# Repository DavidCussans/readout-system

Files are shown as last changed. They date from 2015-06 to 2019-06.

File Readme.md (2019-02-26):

SoLid readout system
====================

_Development of the readout system for the full scale SoLid experiment._

The repository is split into the separate development parts:

* sensors - The light sensors and the PCBs
* analog board - to provide bias voltage, amplify and shape the analog signals form the sensors
* digital board - to digitise the analog signals, analyse the signals in an FPGA to make trigger decisions and transmit them to a PC
* software - to collect data transmitted from the FPGA, further reduce the data and write it to disk. The interface for operators to control the system
* cabling - to connect the senors to the analog board, the analog board to the digital board, power supplies to each board, etc.
* docs - system level documents such as requirements, reports, etc.
* utility_box   design info and documentation about the utility box

Permissions
-----------

The `Readout developers` group have write access, other members of the collaboration have read access.
If you need access contact Dan Saunders.

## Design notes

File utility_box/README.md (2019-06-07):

Tubing Rn dector

thermo tube  4mm inside , 6 mm outside.   To fit it on the rn detector the tube was warmed up.

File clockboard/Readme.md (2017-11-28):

Manufacturing Data for ADC+FPGA Readout Board
=============================================

_Data for PCB fabrication, list of components ( BoM ) , component assembly information._

N.B. This is a copy of information at https://svn2.phy.bris.ac.uk/svn/uob-hep-pc051a

Contains information for :

1) main board
* pc054a_toplevel-manufacturing-artwork-2017-04-27.zip ( Gerber artwork, ODB++ information )
* pc054a_toplevel.pdf ( Circuit schematic )
* pc054a_toplevel_27_assembly.pdf ( Assembly drawings )
* pc054a_toplevel_27.brd ( PCB database file in Cadence Allegro format )
2) FMC ( board that plugs onto FPGA board and couples to main board via VHDCI cable )
* pc054a_fmc-manufacturing-artwork-2017-02-07.zip ( Gerber artwork, ODB++ information )
* pc054a_fmc.pdf ( Circuit schematic )
* pc054a_toplevel_27_assembly.pdf  ( Assembly drawings )
* pc054a_fmc_08.brd ( PCB database file in Cadence Allegro format )

Contains information on how to modify power supply circuit for correct operation:

* pc054a_changes_to_psu.pdf

Contains bitstreams ( with different IP addresses ):

* bitstreams/

Contains prom files ( 4x SPI , s25fl512s-spi-x1_x2_x4 )

* prom_files

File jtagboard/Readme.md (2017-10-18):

Documentation about JTAG board.

Design files in Eagle.

Cable needed to control multiplexer. See https://docs.google.com/spreadsheets/d/1sPC1HHSBhcLIxRam0Nl7j7j9OBzJNn8TZ3wjZsIO86E/edit?usp=sharing

Script to set up Minnowboard GPIO: setup_gpio.sh

Script to select which HDMI interface is used: test_jtag_mltxer.py

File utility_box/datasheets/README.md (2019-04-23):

data sheets for the components used in the utility box. 

for technical info about the sensors and Raspberry Pi see in this repository :
constructiondocs\housing\EnvironmentANDinterlock

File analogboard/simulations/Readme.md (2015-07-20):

#Simulations of the amplifier board

Started by David Cussans and handed over to Wim Beaumont.

Simulations use [LTSpice](http://www.linear.com/designtools/software/) from [Linear Technolgies](http://www.linear.com/)

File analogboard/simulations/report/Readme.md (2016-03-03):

signaldccoupling  : proposal for DC signal coupling between analogue output and ADC

concidencecounts_1.odc  , spread sheet with results from peak finding with two MPPC's . 

related links :

 * presentation 26 jan http://indico.iihe.ac.be/indico/materialDisplay.py?contribId=0&materialId=slides&confId=945 
 * presentation http://indico.iihe.ac.be/indico/materialDisplay.py?contribId=3&materialId=slides&confId=928 
 
oscilloscope_short_2ch.m  : mathlab script to read the oscilloscope and find the peaks and coincidence 

zerrosuppress.m  : mathlab code to read a stored data file and find the nr of samples above thershold. 

# Report on Simulations

To produce write-up:

pdflatex solid_readout_considerations.tex

bibtex solid_readout_considerations.aux

pdflatex solid_readout_considerations.tex

pdflatex solid_readout_considerations.tex

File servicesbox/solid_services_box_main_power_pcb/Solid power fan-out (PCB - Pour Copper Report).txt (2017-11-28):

Pour Copper Report
------------------

Report File:        H:\Projects\SoLid\DCDC Test circuit\Solid Power Fanout\Solid power fan-out (PCB - Pour Copper Report).txt
Report Written:     Wednesday, January 18, 2017
Project Path:       H:\Projects\SoLid\DCDC Test circuit\Solid Power Fanout\Solid power fanout.prj
Design Path:        H:\Projects\SoLid\DCDC Test circuit\Solid Power Fanout\Solid power fan-out.pcb
Design Title:       
Created:            20/09/2016 07:58:07
Last Saved:         18/01/2017 12:43:25
Editing Time:       20600 min
Units:              mm (precision 1)

End Of Report.

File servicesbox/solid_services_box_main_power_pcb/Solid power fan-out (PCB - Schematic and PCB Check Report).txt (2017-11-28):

Schematic and PCB Check Report
------------------------------

Report File:        H:\Projects\SoLid\DCDC Test circuit\Solid Power Fanout\Solid power fan-out (PCB - Schematic and PCB Check Report).txt
Report Written:     Thursday, November 24, 2016
Project Path:       H:\Projects\SoLid\DCDC Test circuit\Solid Power Fanout\Solid power fanout.prj
Design Path:        H:\Projects\SoLid\DCDC Test circuit\Solid Power Fanout\Solid power fan-out.pcb
Design Title:       
Created:            20/09/2016 07:58:07
Last Saved:         31/10/2016 15:54:12
Editing Time:       18976 min
Units:              mm (precision 1)

Checking integrity of Schematic "H:\Projects\SoLid\DCDC Test circuit\Solid Power Fanout\Solid power fan-out.sch" with PCB "H:\Projects\SoLid\DCDC Test circuit\Solid Power Fanout\Solid power fan-out.pcb"
==========================================================================================================================================================================================================

The designs are the same.

End Of Report.

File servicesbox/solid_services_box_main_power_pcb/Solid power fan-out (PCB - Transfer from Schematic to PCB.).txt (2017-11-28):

Transfer from Schematic to PCB.
-------------------------------

Report File:        H:\Projects\SoLid\DCDC Test circuit\Solid power fan-out (PCB - Transfer from Schematic to PCB.).txt
Report Written:     Tuesday, September 20, 2016
Design Path:        H:\Projects\SoLid\DCDC Test circuit\Solid power fan-out.pcb
Design Title:       
Created:            20/09/2016 08:58:07
Last Saved:         20/09/2016 08:58:22
Editing Time:       0 min
Units:              mm (precision 1)

Net class "Power" was not defined, but has been created. Please check the values in the PCB design.

End Of Report.

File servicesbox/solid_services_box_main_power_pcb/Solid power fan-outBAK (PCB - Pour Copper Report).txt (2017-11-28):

Pour Copper Report
------------------

Report File:        H:\Projects\SoLid\DCDC Test circuit\Solid Power Fanout\Solid power fan-outBAK (PCB - Pour Copper Report).txt
Report Written:     Wednesday, October 26, 2016
Project Path:       H:\Projects\SoLid\DCDC Test circuit\Solid Power Fanout\Solid power fanout.prj
Design Path:        H:\Projects\SoLid\DCDC Test circuit\Solid Power Fanout\Solid power fan-outBAK.pcb
Design Title:       
Created:            20/09/2016 08:58:07
Last Saved:         26/10/2016 16:44:35
Editing Time:       12021 min
Units:              mm (precision 1)

End Of Report.

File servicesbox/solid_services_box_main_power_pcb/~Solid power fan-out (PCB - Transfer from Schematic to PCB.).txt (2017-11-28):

Transfer from Schematic to PCB.
-------------------------------

Report File:        H:\Projects\SoLid\DCDC Test circuit\~Solid power fan-out (PCB - Transfer from Schematic to PCB.).txt
Report Written:     Tuesday, September 13, 2016
Design Path:        H:\Projects\SoLid\DCDC Test circuit\~Solid power fan-out.pcb
Design Title:       
Created:            13/09/2016 16:46:20
Last Saved:         13/09/2016 16:46:33
Editing Time:       0 min
Units:              thou (precision 0)

Net class "Power" was not defined, but has been created. Please check the values in the PCB design.

End Of Report.

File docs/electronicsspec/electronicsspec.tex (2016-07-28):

\documentclass[a4paper]{article}

\RequirePackage{graphicx}
\usepackage{authblk}
\usepackage{cleveref}
\crefname{figure}{figure}{figures}
\usepackage{caption}
\usepackage[dvipsnames]{xcolor}
%\usepackage{subcaption}
\usepackage[UKenglish]{babel}
\usepackage{alltt}
\usepackage{afterpage}
\usepackage[text={16cm,25cm},centering]{geometry}
\usepackage{enumitem}
\setenumerate[1]{label=Req. \thesubsection.\arabic*.}
\setenumerate[2]{label=\arabic*.}

%\geometry{
%  a4paper,%
%  top=3cm,%
%  textwidth=16cm,% 
%  textheight=23.2cm,%
%  marginparsep=7pt,% 
%  marginparwidth=2.5cm%
%}

\renewcommand*{\familydefault}{\sfdefault}

\title{Specification for the SoLid read-out electronics}
\author[]{SoLid read-out team}
\newcommand{\version}{Version 1.0}
\date{\today\\\version}

\usepackage{fancyhdr}
\pagestyle{fancy}
\lhead{SoLid read-out electronics specification}
\rhead{\version, \today}

\newcommand{\must}[1]{\textcolor{red}{#1}}
\newcommand{\should}[1]{\textcolor{orange}{#1}}
\def\I2C{I$^2$C}

\begin{document}

\maketitle

\tableofcontents

\section{Introduction}

The SoLid read-out system includes the primary optical sensors (SiPMs), the electronics to control and collect data from them, and the firmware and software used to collect and store this data.
In addition to the SiPM data other data is collected about the temperature and humidity of the detector.

This specification covers the requirements for the PCBs that form the electronic parts of the read-out system:
\begin{itemize}
    \item SiPM boards, which each house a single SiPM sensor
    \item In-detector sensor boards, which house sensors to be deployed inside the detector frames and an in-detector sensor bus interface board, mounted on the frame.
    \item Analog boards, which provide bias control to the sensors and amplify the signals from them.
    \item Digital boards, which digitise the sensor data and feed it into the front-end FPGAs.
    \item Clock distribution boards, which fan-out a global clock to all digital boards.
    \item Power distribution boards, which fan-out power to the analog and digital boards.
    \item FPGA programming boards, which fan out JTAG to program the FPGAs.
\end{itemize}

\subsection{Major versions}

\begin{itemize}
    \item Version 0.0 of this spec is the first version. Minor versions (0.x) have been produced as the system design has evolved.
    \item Version 1.0 (XX Jun 16) of this spec should contain sufficient information to allow the design of the sensor, analog and digital read-out boards. Minor (1.x) versions may be made with the agreement of the team if changes must be made to the specification of analog and digital boards during the design and review phase.
    \item Later major versions will add details to the specification of the other electronics boards (in-detector sensor interface board, in-detector sensor boards, clock distribution board, power distribution board, FPGA programming board).
\end{itemize}

\section{PCB specifications}

The specifications for the various PCBs that will be designed are given in the following subsections.

\subsection{SiPM board}

{\bf Designer: Nick Ryder}

The SiPM boards each house a single SiPM and a connect to two twisted pairs of the SiPM ribbon cable.
One pair provides the bias voltage for the SiPM, the other acts as a ground/voltage reference.

\begin{figure}[h]
    \begin{center}
        
        \caption{Size of the SiPM board.}
        \label{fig:sipmboardsize}
    \end{center}
\end{figure}

\begin{table}[h]
    \begin{center}
        \caption{Pin mapping for the 4-way IDC socket on the SiPM board.}
        \label{tab:IDC4waySiPM}
        \begin{tabular}{cc}
            \hline
            \hline
            Pin & Function \\
            \hline
            1 & GND \\
            2 & GND \\
            3 & SiPM HV \\
            4 & SiPM LV \\
            \hline
            \hline
        \end{tabular}
    \end{center}
\end{table}

\begin{enumerate}
    \item \must{The SiPM board must fit within the existing 3D printed socket design, with dimensions as shown in \cref{fig:sipmboardsize}.}
    \item \must{The SiPM board must house a single S12752-050P SiPM.}
    \item \must{The SiPM board must connect to the SiPM ribbon cable using a 4-way 1.27 mm pitch IDC socket TE 7-188275-4 (Farnell 3784710).}
    \item \must{The 4-way IDE socket must be on the opposite side of the PCB to the SiPM.}
    \item \must{The socket pin connections must be as detailed in \cref{tab:IDC4waySiPM}, where pin 1 is closest to the polarisation pin of the connector. The matching connector on the ribbon cable will be TE 7-215083-4, (Farnell 149032).}
    \item \must{The cable used to connect to the SiPMs must be 1.27 mm pitch twist and flat ribbon cable, with coloured wires (such as 3M XXXX, Farnell XXXX).}
    \item \must{The PCB must be able to identify which specific SiPM sensor is soldered to it.}
    \item \should{The SiPM boards should be designed to ease the production of 3000 units.}
    \item \should{The PCB silkscreen should indicate which order the ribbon cable wires (either coloured or brown) correspond to the IDC socket.}
\end{enumerate}

\clearpage
\newpage
\subsection{In-detector sensor bus}

{\bf Designer: Wim Beaumont (and others?)}

An \I2C bus will be provided on a pair ribbon cables within each detector frame, to allow deployment of in-detector sensors.
Temperature and humidity sensors are expected to be deployed within the detector and other sensors or functionalities may be useful.
The sensor bus ribbon cables will connect to a dedicated sensor bus PCB attached to the covering plate on the detector frame.
This will be deployed below the two analog PCBs.
The 10-way ribbon cable will be split into two in-detector sensor buses.
On bus will have the \I2C and also two GPIO lines, the other will only have \I2C.
The sensor board interface PCB will be connected by a ribbon cable to the digital read-out board's \I2C buses.

\begin{enumerate}
    \item \must{The sensor interface PCB must connect to the two sensor ribbon cables using a 10-way IDC connector, 3M 4610-600 (Farnell 1758627) connector.}
    \item \must{The sensor interface PCB must connect to one 4-way and one 6-way sensor ribbon cable, each with a separate \I2C bus, as shown in \cref{tab:i2cbus}.}
    \item \must{The sensor interface PCB must be able to enable or disable power to the \I2C buses.}
\end{enumerate}

\begin{table}[h]
    \begin{center}
        \caption{Pin mapping for the 10-way IDC socket on the sensor board.}
        \label{tab:i2cbus}
        \begin{tabular}{cc|cc}
            \hline
            \hline
            \multicolumn{2}{c}{Bus 0} & \multicolumn{2}{c}{Bus 1}\\
            Pin & Function & Pin & Function \\
            \hline
            1 & 3.3 V & 7 & 3.3 V \\
            2 & SCL0 & 8 & SCL1 \\
            3 & SDA0 & 9 & SDA1 \\
            4 & GND & 10 & GND \\
            5 & NC / GPIO0? & & \\
            6 & NC / GPIO0? & & \\
            \hline
            \hline
        \end{tabular}
    \end{center}
\end{table}

The sensor boards themselves will potentially have multiple designs to meet the various needs.

\begin{enumerate}
    \item \must{The sensor board must connect to the sensor ribbon cable using either a 6-way 1.27 mm pitch IDC socket (TE 7-188275-6, Farnell 1056234) or a 4-way 1.277 mm IDC socket (TE 7-188275-4, Farnell 3784710).}
    \item \must{The socket pin connections must be as detailed in \cref{tab:indetectorpins}, where pin 1 is closest to the polarisation pin of the connector.}
    \item \must{Each sensor board should allow the selection of \I2C addresses per sensor.}
    \item \should{The cable used for the \I2C bus should be flat ribbon cable, visibly different from the twist and flat cable used for the SiPMs.}
\end{enumerate}

\begin{table}[h]
    \begin{center}
        \caption{Pin mapping for the 4-way and 6-way IDC sockets on the in-detector sensor boards.}
        \label{tab:indetectorpins}
        \begin{tabular}{cc|cc}
            \hline
            \hline
            \multicolumn{2}{c}{6-way bus} & \multicolumn{2}{c}{4-way bus}\\
            Pin & Function & Pin & Function \\
            \hline
            1 & 3.3 V & 1 & 3.3 V \\
            2 & SCL0 & 2 & SCL1 \\
            3 & SDA0 & 3 & SDA1 \\
            4 & GND & 4 & GND \\
            5 & NC / GPIO0? & & \\
            6 & NC / GPIO0? & & \\
            \hline
            \hline
        \end{tabular}
    \end{center}
\end{table}

\clearpage
\newpage
\subsection{Analog board}

{\bf Designer: Wim Beaumont}

The analog boards provide a programmable bias voltage to each SiPM and also amplify the signals from each SiPM.
Two analog boards will be used per detector plane.
All analog boards are identical.

\begin{figure}[h]
    \begin{center}
        
        \caption{Size of the analog board and positions of connectors.}
        \label{fig:analogboardsize}
    \end{center}
\end{figure}

\begin{figure}[h]
    \begin{center}
        
        \caption{Size and positions of both the analog and digital boards.}
        \label{fig:analogdigitalboardsize}
    \end{center}
\end{figure}

%\begin{figure}[h]
%    \begin{center}
%        \includegraphics[width=0.8\textwidth]{imgs/analogboardsize}
%        \caption{Size of the analog board and positions of connectors.}
%        \label{fig:analogboardsize}
%    \end{center}
%\end{figure}

\begin{table}[h]
    \begin{center}
        \caption{Pin mapping for the lower 64-way DIN41612 socket housed on the analog board for connecting to the SiPM ribbon cable. The pin pattern is repeated 16 times. Note that pins A/B1 are towards the lower edge of the board.}
        \label{tab:lowerIDC64way}
        \begin{tabular}{cc|cc}
            \hline
            \hline
            Pin & Function & Pin & Function \\
            \hline
            A(1+2N) & SiPM$_N$ HV & A(2+2N) & GND \\
            B(1+2N) & SiPM$_N$ LV & B(2+2N) & GND \\
            \hline
            \hline
        \end{tabular}
    \end{center}
\end{table}

\begin{table}[h]
    \begin{center}
        \caption{Pin mapping for the upper 64-way DIN41612 socket housed on the analog board for connecting to the SiPM ribbon cable. The pin pattern is repeated 16 times. Note that pins A/B1 are towards the lower edge of the board.}
        \label{tab:upperIDC64way}
        \begin{tabular}{cc|cc}
            \hline
            \hline
            Pin & Function & Pin & Function \\
            \hline
            A(1+2N) & SiPM$_{N+16}$ HV & A(2+2N) & GND \\
            B(1+2N) & SiPM$_{N+16}$ LV & B(2+2N) & GND \\
            \hline
            \hline
        \end{tabular}
    \end{center}
\end{table}

\begin{table}[h]
    \begin{center}
        \caption{Pin mapping for the 3-way low-voltage power connector.}
        \label{tab:LVPower}
        \begin{tabular}{cc}
            \hline
            \hline
            Pin & Function \\
            \hline
            1 & +5 V \\
            2 & GND \\
            3 & -3.3 V \\
            \hline
            \hline
        \end{tabular}
    \end{center}
\end{table}

\begin{table}[h]
    \begin{center}
        \caption{Pin mapping for the 2-way high-voltage power connector.}
        \label{tab:HVPower}
        \begin{tabular}{cc}
            \hline
            \hline
            Pin & Function \\
            \hline
            1 & HV $\le 80 V$ \\
            2 & GND \\
            \hline
            \hline
        \end{tabular}
    \end{center}
\end{table}

%\begin{table}[h]
%    \begin{center}
%        \caption{Pin mapping for the 10-way IDC socket housed on the analog board for connecting to the in-detector I2C bus.}
%        \label{tab:IDC10way}
%        \begin{tabular}{cc|cc|cc|cc|cc}
%            \hline
%            \hline
%            Pin & Function & Pin & Function & Pin & Function & Pin & Function & Pin & Function \\
%            \hline
%            1 & GND & 3 & 3.3 V & 5 & NC & 7 & GND & 9 & 3.3 V \\
%            2 & SDA0 & 4 & SCL0 & 6 & NC & 8 & SDA1 & 10 & SDA1 \\
%            \hline
%            \hline
%        \end{tabular}
%    \end{center}
%\end{table}

\begin{table}[h]
    \begin{center}
        \caption{Pin mapping for the upper 96-way DIN socket connecting the analog to the digital board. Note that pins A/B/C1 are towards the lower edge of the board.}
        \label{tab:DIN96Upper}
        \begin{tabular}{cc|cc|cc}
            \hline
            \hline
            Pin & Function & Pin & Function & Pin & Function \\
            \hline
            A1 & GND & B1 & GND & C1 & GND \\
            A2 & A16+ & B2 & GND & C2 & A17+ \\
            A3 & A16- & B3 & GND & C3 & A17- \\
            A4 & GND & B4 & GND & C4 & GND \\
            A5 & A18+ & B5 & GND & C5 & A19+ \\
            A6 & A18- & B6 & GND & C6 & A19- \\
            A7 & GND & B7 & GND & C7 & GND \\
            A8 & A20+ & B8 & GND & C8 & A21+ \\
            A9 & A20- & B9 & GND & C9 & A21- \\
            A10 & GND & B10 & GND & C10 & GND \\
            A11 & A22+ & B11 & GND & C11 & A23+ \\
            A12 & A22- & B12 & GND & C12 & A23- \\
            A13 & GND & B13 & GND & C13 & GND \\
            A14 & A24+ & B14 & GND & C14 & A25+ \\
            A15 & A24- & B15 & GND & C15 & A25- \\
            A16 & GND & B16 & GND & C16 & GND \\
            A17 & A26+ & B17 & GND & C17 & A27+ \\
            A18 & A26- & B18 & GND & C18 & A27- \\
            A19 & GND & B19 & GND & C19 & GND \\
            A20 & A28+ & B20 & GND & C20 & A29+ \\
            A21 & A28- & B21 & GND & C21 & A29- \\
            A22 & GND & B22 & GND & C22 & GND \\
            A23 & A30+ & B23 & GND & C23 & A31+ \\
            A24 & A30- & B24 & GND & C24 & A31- \\
            A25 & GND & B25 & GND & C25 & GND \\
            A26 & GPIO2 & B26 & GND & C26 & GPIO3 \\
            A27 & +3.3 V & B27 & GND & C27 & +1.8 V \\
            A28 & GND & B28 & GND & C28 & GND \\
            A29 & SDA0 & B29 & GND & C29 & SCL0 \\
            A30 & GND & B30 & GND & C30 & GND \\
            A31 & GND & B31 & GND & C31 & GND \\
            A32 & +5 V & B32 & GND & C32 & +5 V \\
            \hline
            \hline
        \end{tabular}
    \end{center}
\end{table}

\begin{table}[h]
    \begin{center}
        \caption{Pin mapping for the lower 96-way DIN socket connecting the analog to the digital board. Note that pin A/B/C1 are towards the lower edge of the board.}
        \label{tab:DIN96Lower}
        \begin{tabular}{cc|cc|cc}
            \hline
            \hline
            Pin & Function & Pin & Function & Pin & Function \\
            \hline
            A1 & GND & B1 & GND & C1 & GND \\
            A2 & A0+ & B2 & GND & C2 & A1+ \\
            A3 & A0 & B3 & GND & C3 & A1- \\
            A4 & GND & B4 & GND & C4 & GND \\
            A5 & A2+ & B5 & GND & C5 & A3+ \\
            A6 & A2- & B6 & GND & C6 & A3- \\
            A7 & GND & B7 & GND & C7 & GND \\
            A8 & A4+ & B8 & GND & C8 & A5+ \\
            A9 & A4- & B9 & GND & C9 & A5- \\
            A10 & GND & B10 & GND & C10 & GND \\
            A11 & A6+ & B11 & GND & C11 & A7+ \\
            A12 & A6- & B12 & GND & C12 & A7- \\
            A13 & GND & B13 & GND & C13 & GND \\
            A14 & A8+ & B14 & GND & C14 & A9+ \\
            A15 & A8- & B15 & GND & C15 & A9- \\
            A16 & GND & B16 & GND & C16 & GND \\
            A17 & A10+ & B17 & GND & C17 & A11+ \\
            A18 & A10- & B18 & GND & C18 & A11- \\
            A19 & GND & B19 & GND & C19 & GND \\
            A20 & A12+ & B20 & GND & C20 & A13+ \\
            A21 & A12- & B21 & GND & C21 & A13- \\
            A22 & GND & B22 & GND & C22 & GND \\
            A23 & A14+ & B23 & GND & C23 & A15+ \\
            A24 & A14- & B24 & GND & C24 & A15- \\
            A25 & GND & B25 & GND & C25 & GND \\
            A26 & GPIO0 & B26 & GND & C26 & GPIO1 \\
            A27 & +3.3 V & B27 & GND & C27 & +1.8 V \\
            A28 & GND & B28 & GND & C28 & GND \\
            A29 & SDA1 & B29 & GND & C29 & SCL1 \\
            A30 & GND & B30 & GND & C30 & GND \\
            A31 & GND & B31 & GND & C31 & GND \\
            A32 & +5 V & B32 & GND & C32 & +5 V \\
            \hline
            \hline
        \end{tabular}
    \end{center}
\end{table}

\begin{enumerate}
    \item \must{The analog board height (as shown in \cref{fig:analogboardsize}) must be 220 mm.}
    \item \should{The analog board width should be 150 mm.}
    \item \must{The analog board must connect to two 16-SiPM ribbon cables via a 64-way 1.27mm pitch DIN41612 plug connector each (Farnell 1096830).}
    \item \must{The pin mapping for each IDC socket connectiong to the SiPM ribbon cables must be as described in \cref{tab:lowerIDC64way,tab:upperIDC64way}, with pin1 on the lower edge of the connector and row A {\bf on which side?}.}
    \item \must{The analog board must connect to the digital board using two 96-way DIN41612 socket connectors (Farnell 1096942).}
    \item \must{The pin mapping for the two connectors to the digital board must be as described in \cref{tab:DIN96Upper,tab:DIN96Lower}, with pins A/B/C1 on the lower edge of the connector and row A {\bf on which side?}}
    \item \must{The position of the two connectors to the digital board must be as shown in \cref{fig:analogboardsize}.}
    \item \must{The analog board must use input power connections of -3.1, GND, + 4.7 V (supplied by remote -3.3 V and +5 V power supplies), using a Molex 22-23-2031 connector (Farnell 1462950).}
    \item \must{The pin mapping for the low voltage connector must be as shown in \cref{tab:LVPower}, where pin 1 is defined as the left-most pin when the polarising shroud is upper-most.}
    \item \must{The analog board must regulate the input power to -2.8, GND, +4.4 V using linear regulators.}
    \item \must{The regulators must be controllable from the digital board to enable or disable powering the analog board components.}
    \item \must{The analog board must amplify the signal from each of 32 SiPMs using an AD8132 amplifier.}
    \item \should{The analog board should be compatible with replacing the DC connection to the digital board with an AC connection by replacing only passive components and not using the negative voltage power supply.}
    \item \must{The analog board must use high voltage input connections using a connector that is incompatible with the low voltage connector (perhaps JST VHR-2N (RS 820-1172).}
    \item \must{The pin mapping of the high voltage input must be as shown in \cref{fig:HVPower}, where pin 1 is defined as...}
    \item \must{A fuse must be used to protect the board from excessive current from the HV supply, to break at $I \le 100$ mA.}
    \item \should{The high- and low-voltage supply connectors should be clearly labelled on the PCB.}
    \item \must{The analog board must be able to produce a programmable high voltage bias supply on board, using ADL5317.}
    \item \must{The analog board must provide a per SiPM low voltage trim of up to 4 V using programmable DACs.}
    \item \must{The programmable DACs must be controllable by from the digital board via the \I2C buses on the two 96-way connectors.}
    \item \should{The channel numbering of the DACs should map simply to the channel numbering of the SiPMs.}
    \item \must{The analog board must provide an on-board temperature measurement and unique ID using an ATMEL AT30TSE752 chip with an \I2C address of 0b1001000 (i.e. all address pins connected to GND).} 
    \item \should{The temperature alert line from the temperature chip should be connected to one of the GPIO pins on the 96-way DIN connectors.}
\end{enumerate}

\clearpage
\newpage

\subsection{Digital board}

{\bf Designer: David Cussans}

The digital boards house an FPGA board which does front end processing and triggering.
They also digitise the amplified signals from the analog boards.
Each detector plane will use a single digital board, receiving data from two analog boards, as shown in \cref{fig:analogdigitalboardsize}.

%\begin{figure}[h]
%    \begin{center}
%        \includegraphics[width=0.8\textwidth]{imgs/digitalboardsize}
%        \caption{Size of the digital board and positions of connectors.}
%        \label{fig:digitalboardsize}
%    \end{center}
%\end{figure}

\begin{table}[h]
    \begin{center}
        \caption{LVDS pins available for ADC data on the Trenz 0712.}
        \label{tab:TrenzLVDS}
        \begin{tabular}{cccc}
            \hline
            \hline
            Connector & Bank & Pairs & \# Pairs \\
            \hline
            JM1 & 13 & 3, 5, 6, 9, 11 & 5 \\
            %JM1 & 16 & 16, 19, 17, 18, 9, 7, 11, 10, 5, 2, 6, 4, 1, 22, 24, 23, 15, 20, 21, 13, 14, 3, 12, 8 &  24 & 29 \\
            JM1 & 16 & 1-24 & 24 \\
            JM2 & 13 & 1, 2, 4, 10, 12-17 & 10 \\
            JM3 &  15 & 1-24 & 24 \\
            \hline
            \multicolumn{3}{c}{Total} & 63 \\
            \hline
            \hline
        \end{tabular}
    \end{center}
\end{table}

\begin{table}[h]
    \begin{center}
        \caption{Pin uses for Trenz 0712 bank 14 (3.3 V).}
        \label{tab:TrenzB14}
        \begin{tabular}{cc}
            \hline
            \hline
            Usage & \# pins \\
            \hline
            1 channel ADC data & 2 \\
            CPLD \I2C/SPI device select & 5 \\
            CPLD SPI (MOSI, MISO, CLK) or \I2C (SCL, SDAI, SDAO) & 3 \\
            %CPLD \I2C (SCL, SDAI, SDAO) & 3 \\
            Analog board GPIO & 8 \\
            LEDs & 4 \\
            IP address switches & 8 \\
            \hline
            Total & 30 / 30 \\
            \hline
            \hline
        \end{tabular}
    \end{center}
\end{table}

\begin{table}[h]
    \begin{center}
        \caption{Pin information for the HDMI connector used for the clock and synchronisation signals.}
        \label{tab:ClockSyncPins}
        \begin{tabular}{cc|cc|cc}
            \hline
            \hline
            Pin & Function & Pin & Function & Pin & Function \\
            \hline
            1 & SYNC+ & 2 & SYNC shield  & 3 & SYNC- \\
            4 & NC? & 5 & NC? & 6 & NC? \\
            7 & CLK+ & 8 & CLK shield & 9 & CLK- \\
            10 & NC? & 11 & NC? & 12 & NC? \\
            13 & Power Enable? & 14 & NC? & 15 & NC? \\
            16 & NC? & 17 & NC? & 18 & NC? \\
            19 & NC? & & & & \\
            \hline
            \hline
        \end{tabular}
    \end{center}
\end{table}

\begin{table}[h]
    \begin{center}
        \caption{Pin mapping for the connection between the digital board and \I2C interface board. {\bf To be defined...}}
        \label{tab:digitalToI2CInterface}
        \begin{tabular}{cc|cc}
            \hline
            \hline
            Pin & Function & Pin & Function \\
            \hline
            1 & ? & 6 & ? \\
            2 & ? & 7 & ? \\
            3 & ? & 8 & ? \\
            4 & ? & 9 & ? \\
            5 & ? & 10 & ? \\
            \hline
            \hline
        \end{tabular}
    \end{center}
\end{table}

\begin{enumerate}
    \item \should{The digital board height (as shown in \cref{fig:analogdigitalboardsize}) should be 466.2 mm.}
    \item \should{The digital board width should be 160 mm.}
    \item \must{The digital board must connect to the analog boards using two 96-way DIN41612 plug connectors (Farnell 1096905).}
    \item \must{The pin mapping for the connectors to the analog board must be as described in \cref{tab:DIN96Upper,tab:DIN96Lower}.}
    \item \must{The position of the two 96-way DIN41612 connectors must allow the analog boards' connectors to be be as shown in \cref{fig:analogboardsize}, with the spacing between the two analog boards as shown in \cref{fig:analogdigitalboardsize}.}
    \item \must{The digital board must allow a Trenz 0712 board to be plugged in.}
    \item \must{The pin usage/mapping for the Trenz board connections must be as shown in \cref{tab:TrenzLVDS,tab:TrenzB14}.}
    \item \must{The digital board must digitise 64 SiPM channels using 8 LTM9007 ADCs.}
    \item \must{The ADCs must be controlled via a 16-channel SPI-like bus, with two chip select lines per ADC chip.}
    \item \must{The digital board must have an HDMI connector to receive a clock and synchronisation signal, with the pin connection as shown in \cref{tab:ClockSyncPins}.}
    \item \must{The digital board must have an on board SiXXXX chip to clean the external clock signal and provide the clocks for the ADC chips and FPGA.}
    \item \must{The SiXXXX clock chip must be controlled by an \I2C bus on the digital board.}
    \item \must{The digital board must have an SFP+ cage for a Gbps Ethernet connection.}
    \item \must{The digital board must use input power connections of GND and 5 V.}
    \item \must{The digital board must convert the input power to 1.8 V and 3.3 V using on-board switching DC-DC converters.}
    \item \must{The DC-DC converters must be controllable from the FPGA, to enable/disable powering of the ADC.}
    \item \must{The powering of the FPGA should be controllable remotely via a control line on the HDMI clock/sync bus.}
    \item \must{The digital board should include a temperature sensor that can power down the FPGA if the board temperature exceeds a programmable alarm threshold.}
    \item \must{The digital board must have two eSATA sockets to allow Gbps serial communications between FPGAs from neighbouring planes.}
    \item \must{The digital board must have a 10-way IDC ribbon cable socket to connect to the in-detector sensor \I2C interface board.}
    \item \must{The connections to the \I2C interface board should be as defined in \cref{tab:digitalToI2CInterface}.}
\end{enumerate}

\clearpage
\newpage
\subsection{Clock distribution board}

{\bf Designer: David Cussans}

The clock distribution board provides the same clock to all digital boards.
In addition the board is able to provide a synchronous pulsed signal to all boards to ensure synchronisation across the detector.

\begin{enumerate}
    \item \must{The clock distribution board must provide a xxx MHz clock to all digital boards.}
    \item \must{The clock distribution board must provide a pulse signal synchronously to ten digital boards.}
    \item \must{It must be possible to enable or disable the synchronisation pulses from software.}
    \item \must{The clock and synchronisation signals must be provided via an HDMI connector.}
    \item \must{The HDMI connector pin mapping must be as shown in \cref{tab:ClockSyncPins}.}
    \item \must{The clock distribution system must have a hierarchical design. Each module of 10 detector planes should be served by a single clock distribution board, which in turn is served by a global 1:10 clock distribution board.}
    \item \should{The FPGA controlling the clock system should have a firmware tool chain compatible with the Artix-7 that will be used on the read-out board.}
\end{enumerate}

\clearpage
\newpage
\subsection{Power distribution board}

{\bf Designer: ?}

Power distribution boards should provide ten detector planes with the necessary high and low voltage power...

\clearpage
\newpage
\subsection{FPGA programming board}

{\bf Designer: Bristol electronics design group}

Each module of ten detector planes will have an FPGA programming board.
This will house a network accessible computer running the Xilinx programming software.
The board will fan out JTAG connections to each of the ten FPGAs in the detector module.

\clearpage
\newpage

\section{Review process}

The analog and digital schematics will be internally reviewed.
Following completion of the lay out for the two boards they will be reviewed by internal and external reviewers.
This review will have a larger scope, including the system level design of the read-out system.

\section{Time schedule}

This is the time schedule discussed at the collaboration meeting at Imperial in May 2016.
It is based around designing and reviewing the design before producing sufficient electronics to instrument 5 detector planes.
These will then be tested and validated before starting a larger production for 50 planes.

\begin{figure}[h]
    \begin{center}
        
        \caption{Estimated schedule, where task 10 corresponds to the electronics described in this specification.}
        \label{fig:gantt}
    \end{center}
\end{figure}

\end{document}

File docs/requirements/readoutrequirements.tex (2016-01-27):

\documentclass[a4paper]{article}

\RequirePackage{graphicx}
\usepackage{authblk}
%\usepackage{cleveref}
\usepackage{caption}
%\usepackage{subcaption}
\usepackage[UKenglish]{babel}
\usepackage{alltt}
\usepackage{afterpage}
\usepackage[text={16cm,25cm},centering]{geometry}

%\geometry{
%  a4paper,%
%  top=3cm,%
%  textwidth=16cm,% 
%  textheight=23.2cm,%
%  marginparsep=7pt,% 
%  marginparwidth=2.5cm%
%}

\renewcommand*{\familydefault}{\sfdefault}

\title{Requirements for the SoLid read-out system}
\author[]{SoLid collaboration}
\date{\today\\V0.2}

\begin{document}

\maketitle

\tableofcontents

\section{Introduction}

This document defines the requirements for the full scale SoLid experiment's read-out system (the scope of which is defined below).
The purpose of the requirements is to ensure that the read-out system that will be produced will perform the necessary functionality for the SoLid experiment to be successful.
Two forms of requirements are defined.
Mandatory requirements use the term `must', whilst the term `should' is used for requirements which are desirably but not mandatory.
The requirements constrain the the overall design of the system, but should not constrain specific implementations.
For example, it is a requirement that there be a neutron trigger but not a requirement that a specific algorithm be used for the trigger.
During the design phase of the read-out system development the requirements may be updated, but once the initial version is agreed by the collaboration it is hoped that major changes will not be required.

\subsection{Scope of the read-out system}

The read out system includes the photo sensors (likely Silicon Photomultipliers or SiPMs), all electronics used to bias the sensors and store data collected from them, the software used to control the electronics,  the computing systems and software used to store and transmit the data out of SCK and the user interfaces to that software. 
The read out system does not include the scintillators, wavelength shifting fibres, mechanical frames, shielding, etc. that forms the physical detector. 
The read out system also does not include any software or computing systems used for data analysis or storage once the data is transmitted out of SCK.

\section{Requirements}

The requirements are split into a number of categories.
The physics requirements are those that are constrained by the need to perform the physics analyses (an oscillation search and spectrum measurement) planned for the experiment.
The infrastructure requirements are constrained by the infrastructure availability at BR2.
The operational requirements define how an operator should be able to control the experiment.
The budget requirements cover the time and cost constraints on the system.

\subsection{Physics requirements}

\renewcommand*{\theenumi}{\thesubsection.\arabic{enumi}}
\renewcommand*{\theenumii}{\thesubsection.\arabic{enumii}}
\begin{enumerate}
\item Neutron trigger - The system must be able to trigger on neutron signals coming from one vertical and one horizontal fibre in the same plane. 
    The neutron trigger should be x \% efficient for neutrons captured in the $^6$LiF:ZnS(Ag) layer. 
    For each neutron trigger the system must be able to store at least 0.5 ms of data from relevant channels around the neutron ID. 
    These requirements will ensure that the IBD trigger efficiency is independent of the positron energy and that the trigger rate does not strongly depend upon background signal rates.
\item Threshold trigger - The system must be able to trigger when a signal above a defined threshold is detected from one or more fibres in coincidence.
    This will allow measurement of efficiency of the neutron trigger and calibration running without neutron signals.
\item Random trigger -  The system must be able to be randomly triggered. 
    This will allow measurements of low amplitude signals.
\item Cosmic muon trigger - The system should be able to trigger on a the signal from a cosmic ray muon crossing many scintillator cubes. 
    For each cosmic ray trigger the system must be able to store relevant data in a time window around the trigger. 
    This will allow studies of cosmic ray related background events.
\item Energy range - Each channel must have a large enough range that a cosmic muon crossing a horizontal fibre does not normally saturate the range. 
    This will allow the use of cosmic rays for energy calibration. 
\item Channel resolution - Each channel must have a high enough resolution that the single photon amplitude can be measured. 
    This will allow the channel uniformity and stability to be measured and ensure that the read out system does not limit the energy resolution of the detector.
\item Noise - The read out system will introduce analog and digital noise to the signals from the sensors. 
    The combined noise from the read out system must be less than a single photon detection and should be less than 0.1 photons.
\item Channel uniformity - The readout system must be capable of supplying all channels with an over voltage that is uniform within x \%. 
    This will limit systematic variations in the measurement of IBD candidates at different locations within the detector.
\item Channel stability - The readout system must be cable of maintaining an over voltage that is stable within x \% over the five years of operation. 
    This will limit systematic variations in the measurement of IBD candidates in reactor on/off cycles.
\item Dead time - The system should not have any dead time. The system must store information to allow the calculation of the amount of dead time, the time at which it occurred and the channels effected.
\item Number of channels - The system must be capable of scaling up to take data from at least 6000 channels. 
    This will allow the detector volume to be increased using the same read out design should additional modules be funded.  
\item Experiment duration - The system should be capable of running for five years. 
    This will allow a sensitive search for short baseline oscillations.
\item Data required - The system must store the following data: 
    \begin{itemize}
    \item The time, position and waveform for signals identified as neutrons
    \item Enough data to extract the time, position and number of photons of any signals identified as coming from the PVT within a time window of -x and +y around the neutron trigger
    \item The over voltage supplied to all channels at all times during the experiment.
    \item The temperature and any other local conditions measured during the experiment.
    \item The start/end times and the trigger conditions for any data run.   
    \end{itemize}
    This will provide enough information to perform an oscillation analysis.
\end{enumerate}

\subsection{Infrastructure requirements}

\begin{enumerate}
\item A single optical Ethernet connection can be used to transfer data from the detector to the computing room at BR2.
\item x is provided to power the read out system.
\item The total bandwidth of data transmitted out of SCK should be limited to x GB/day.
\item x, y, z are not allowed within the containment building.
\end{enumerate}

\subsection{Operational requirements}

\begin{enumerate}
\item Operators must be able to set a uniform over voltage on a set of channels. 
\item Operators must be able to set a uniform bias voltage on a set of channels.
\item Updating the bias voltage of all channels should take less than 30 s.
\item Operators must be able to start and stop a data taking run defining:
    \begin{enumerate}
    \item The trigger conditions for the run
    \item The duration of the run
    \item The channels included in the run
    \end{enumerate}
\item Operators must be able to view the current state of the detector and any ongoing run.
\item Operators must be able to view the historic state of the detector and any previous runs. 
\item The system must not require constant supervision.
\item The system should run autonomously, sending out alerts to operators when failures occur.
\item The system should be operable from outside of SCK.
\end{enumerate}

\subsection{Budget requirements}

This section currently covers the budget requirements for the first phase of the detector deployment, funded by the Belgian research council. 
The total costs below should include the purchase of parts and any workshop time required to assemble the electronics.
\begin{enumerate}
\item The first phase of the experiment must be deployed by x (date) and should be deployed by y (date). 
\item The total cost of the read out system for the first phase must be less than x euro and should be less than y euro.
\item The read out system must cost less than x euro per channel and should cost less than y euro per channel.
\end{enumerate}

\end{document}

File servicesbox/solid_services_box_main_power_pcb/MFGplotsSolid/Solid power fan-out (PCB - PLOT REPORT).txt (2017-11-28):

PLOT REPORT
-----------

Report File:        H:\Projects\SoLid\DCDC Test circuit\Solid Power Fanout\Solid power fan-out (PCB - PLOT REPORT).txt
Report Written:     Thursday, March 02, 2017
Project Path:       H:\Projects\SoLid\DCDC Test circuit\Solid Power Fanout\Solid power fanout.prj
Design Path:        H:\Projects\SoLid\DCDC Test circuit\Solid Power Fanout\Solid power fan-out.pcb
Design Title:       
Created:            20/09/2016 07:58:07
Last Saved:         14/02/2017 13:44:44
Editing Time:       22663 min
Units:              mm (precision 1)

Device Settings
===============

Gerber Settings
===============

    Leading zero suppression.
    G01 assumed throughout.
    Line termination <*> <CR> <LF>.
    2.3 format absolute inches.

    Format commands defined in Gerber file.
    Aperture table defined in Gerber file.
    Hardware arcs allowed.

Drill Settings
==============

    Excellon Format 1    Format 2.3 absolute in mm.
    No zero suppression.

Plots Output
============

Gerber Output
=============

H:\Projects\SoLid\DCDC Test circuit\Solid Power Fanout\Solid power fan-out - Top Silkscreen.gbr

    Layers:
    ------------------
    Top Silkscreen
    Board Outlines

    D-Code Shape  (thou)
    -----------------------
    D10    Round 12.00
    D16    Round 5.00
    D84    Round 6.00
    D85    Round 3.00

Gerber Output
=============

H:\Projects\SoLid\DCDC Test circuit\Solid Power Fanout\Solid power fan-out - Top Copper.gbr

    Layers:
    --------------
    Top Copper

    D-Code Shape  (thou)
    ----------------------------------------------
    D10    Round 12.00
    D11    Round 10.00
    D15    Round 100.00
    D17    Round 196.85
    D18    Round 80.00
    D19    Round 200.00
    D71    Rectangle 74.00 X 98.00  Rotation 90
    D20    Square 52.00
    D21    Round 52.00
    D23    Round 78.74
    D25    Round 125.98
    D26    Round 39.37
    D27    Round 40.00
    D28    Round 137.80
    D88    Round 59.06
    D89    Round 250.00
    D90    Square 60.00
    D91    Round 60.00
    D92    Round 141.73
    D96    Round 110.00
    D97    Rectangle 74.00 X 98.00
    D98    Round 98.43

Gerber Output
=============

H:\Projects\SoLid\DCDC Test circuit\Solid Power Fanout\Solid power fan-out - Top Copper (Resist).gbr

    Layers:
    --------------
    Top Copper

    D-Code Shape  (thou)
    -----------------------------------------------
    D72    Round 206.85
    D73    Round 90.00
    D74    Round 210.00
    D76    Rectangle 84.00 X 108.00  Rotation 90
    D77    Square 62.00
    D78    Round 62.00
    D80    Round 88.74
    D81    Round 110.00
    D93    Round 260.00
    D94    Square 70.00
    D95    Round 70.00
    D99    Round 120.00
    D100   Rectangle 84.00 X 108.00

Gerber Output
=============

H:\Projects\SoLid\DCDC Test circuit\Solid Power Fanout\Solid power fan-out - Top Copper (Paste).gbr

    Layers:
    --------------
    Top Copper

    D-Code Shape  (thou)
    ----------------------------------------------
    D83    Rectangle 70.00 X 94.00  Rotation 90
    D101   Rectangle 70.00 X 94.00

Gerber Output
=============

H:\Projects\SoLid\DCDC Test circuit\Solid Power Fanout\Solid power fan-out - Layer 2 Copper.gbr

    Layers:
    ------------------
    Layer 2 Copper

    D-Code Shape  (thou)
    -----------------------
    D10    Round 12.00
    D15    Round 100.00
    D16    Round 5.00
    D17    Round 196.85
    D18    Round 80.00
    D19    Round 200.00
    D20    Square 52.00
    D21    Round 52.00
    D23    Round 78.74
    D27    Round 40.00
    D88    Round 59.06
    D89    Round 250.00
    D90    Square 60.00
    D91    Round 60.00
    D96    Round 110.00
    D102   Round 23.62

Gerber Output
=============

H:\Projects\SoLid\DCDC Test circuit\Solid Power Fanout\Solid power fan-out - Layer 3 Copper.gbr

    Layers:
    ------------------
    Layer 3 Copper

    D-Code Shape  (thou)
    -----------------------
    D10    Round 12.00
    D15    Round 100.00
    D16    Round 5.00
    D17    Round 196.85
    D18    Round 80.00
    D19    Round 200.00
    D20    Square 52.00
    D21    Round 52.00
    D23    Round 78.74
    D27    Round 40.00
    D88    Round 59.06
    D89    Round 250.00
    D90    Square 60.00
    D91    Round 60.00
    D96    Round 110.00

Gerber Output
=============

H:\Projects\SoLid\DCDC Test circuit\Solid Power Fanout\Solid power fan-out - Layer 4 Copper.gbr

    Layers:
    ------------------
    Layer 4 Copper

    D-Code Shape  (thou)
    -----------------------
    D10    Round 12.00
    D15    Round 100.00
    D16    Round 5.00
    D17    Round 196.85
    D18    Round 80.00
    D19    Round 200.00
    D20    Square 52.00
    D21    Round 52.00
    D23    Round 78.74
    D27    Round 40.00
    D88    Round 59.06
    D89    Round 250.00
    D90    Square 60.00
    D91    Round 60.00
    D96    Round 110.00

Gerber Output
=============

H:\Projects\SoLid\DCDC Test circuit\Solid Power Fanout\Solid power fan-out - Layer 5 Copper.gbr

    Layers:
    ------------------
    Layer 5 Copper

    D-Code Shape  (thou)
    -----------------------
    D10    Round 12.00
    D15    Round 100.00
    D16    Round 5.00
    D17    Round 196.85
    D18    Round 80.00
    D19    Round 200.00
    D20    Square 52.00
    D21    Round 52.00
    D23    Round 78.74
    D27    Round 40.00
    D88    Round 59.06
    D89    Round 250.00
    D90    Square 60.00
    D91    Round 60.00
    D96    Round 110.00

Gerber Output
=============

H:\Projects\SoLid\DCDC Test circuit\Solid Power Fanout\Solid power fan-out - Bottom Copper.gbr

    Layers:
    -----------------
    Bottom Copper

    D-Code Shape  (thou)
    -----------------------
    D10    Round 12.00
    D15    Round 100.00
    D16    Round 5.00
    D17    Round 196.85
    D18    Round 80.00
    D19    Round 200.00
    D20    Square 52.00
    D21    Round 52.00
    D23    Round 78.74
    D27    Round 40.00
    D88    Round 59.06
    D89    Round 250.00
    D90    Square 60.00
    D91    Round 60.00
    D92    Round 141.73
    D96    Round 110.00

Gerber Output
=============

H:\Projects\SoLid\DCDC Test circuit\Solid Power Fanout\Solid power fan-out - Bottom Copper (Resist).gbr

    Layers:
    -----------------
    Bottom Copper

    D-Code Shape  (thou)
    -----------------------
    D72    Round 206.85
    D73    Round 90.00
    D74    Round 210.00
    D77    Square 62.00
    D78    Round 62.00
    D80    Round 88.74
    D81    Round 110.00
    D93    Round 260.00
    D94    Square 70.00
    D95    Round 70.00
    D99    Round 120.00

Gerber Output
=============

H:\Projects\SoLid\DCDC Test circuit\Solid Power Fanout\Solid power fan-out - Bottom Copper (Paste).gbr

    Layers:
    -----------------
    Bottom Copper

    D-Code Shape  (thou)
    -----------------------

Gerber Output
=============

H:\Projects\SoLid\DCDC Test circuit\Solid Power Fanout\Solid power fan-out - Bottom Silkscreen.gbr

    Layers:
    ---------------------
    Bottom Silkscreen

    D-Code Shape  (thou)
    -----------------------
    D10    Round 12.00

NC Drill Output
===============

H:\Projects\SoLid\DCDC Test circuit\Solid Power Fanout\Solid power fan-out - Drill Data - [Through Hole].drl

    Output:
    ---------------------------
    Plated Round Drill Holes
    Plated Slots
    Plated Board Outlines

    Tool  Size      Count   ID
    ---------------------------------
    T001  00.024 in 36    K
    T002  00.032 in 6     F
    T003  00.038 in 9     M
    T004  00.040 in 9     N
    T005  00.043 in 21    C
    T006  00.047 in 198   H
    T007  00.052 in 126   I
    T008  00.082 in 6     D
    T009  00.130 in 12    E
    T010  00.138 in 28    L
    ---------------------------------
    Total           451
    ---------------------------------

H:\Projects\SoLid\DCDC Test circuit\Solid Power Fanout\Solid power fan-out - Drill Data - [Through Hole] (Unplated).drl

    Output:
    -----------------------------
    Unplated Round Drill Holes
    Unplated Slots
    Unplated Board Outlines

    Tool  Size      Count   ID
    ---------------------------------
    T001  00.025 in 1
    ---------------------------------
    Total           1
    ---------------------------------

Gerber Output
=============

H:\Projects\SoLid\DCDC Test circuit\Solid Power Fanout\Solid power fan-out - Drill Ident Drawing - [Through Hole].gbr

    Layers:
    ------------------
    [Through Hole]

Drill Ident Drawing
===================

    Drill Plated Size Shape ID
    -----------------------------------
    43    Y      100  Round C
    82    Y      100  Round D
    130   Y      100  Round E
    32    Y      100  Round F
    47    Y      100  Round H
    52    Y      100  Round I
    24    Y      100  Round K
    138   Y      100  Round L
    38    Y      100  Round M
    40    Y      100  Round N

    D-Code Shape  (thou)
    -----------------------
    D15    Round 100.00
    D16    Round 5.00

End Of Report.

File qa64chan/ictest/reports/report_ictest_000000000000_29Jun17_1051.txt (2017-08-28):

Time: 29Jun17_1051
Tester: nr16874
Board: 000000000000
Address: 
Tests:
	Contact:	failure
	UniqueID:	
	DigitalI2C:	
	PowerChips:	
	Voltages:	
	Currents:	
	LM82Temp:	
	InDetectorI2C:	
	Temperature:	
	ADCControl:	
	Analog0I2C:	
	Analog1I2C:	
	ClockSA:

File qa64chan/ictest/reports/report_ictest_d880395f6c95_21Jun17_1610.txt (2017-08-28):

Time: 21Jun17_1610
Tester: nr16874
Board: d880395f6c95
Tests:
	Contact:	success
	UniqueID:	success
	DigitalI2C:	success
	PowerChips:	success
	Voltages:	success
	Currents:	success
	LM82Temp:	success
	InDetectorI2C:	warning
	Temperature:	success
	ADCControl:	success
	Analog0I2C:	success
	Analog1I2C:	success

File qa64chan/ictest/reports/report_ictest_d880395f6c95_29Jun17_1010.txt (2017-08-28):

Time: 29Jun17_1010
Tester: nr16874
Board: d880395f6c95
Tests:
	Contact:	success
	UniqueID:	success
	DigitalI2C:	success
	PowerChips:	success
	Voltages:	success
	Currents:	success
	LM82Temp:	success
	InDetectorI2C:	failure
	Temperature:	success
	ADCControl:	success
	Analog0I2C:	success
	Analog1I2C:	success
	ClockSA:	success

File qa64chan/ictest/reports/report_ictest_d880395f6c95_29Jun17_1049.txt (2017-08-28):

Time: 29Jun17_1049
Tester: nr16874
Board: d880395f6c95
Tests:
Address: 3139322e3136382e3233352e313a3530303031
Tests:
	Contact:	success
	UniqueID:	success
	DigitalI2C:	success
	PowerChips:	success
	Voltages:	success
	Currents:	success
	LM82Temp:	success
	InDetectorI2C:	warning
	Temperature:	success
	ADCControl:	success
	Analog0I2C:	success
	Analog1I2C:	success
	ClockSA:	success

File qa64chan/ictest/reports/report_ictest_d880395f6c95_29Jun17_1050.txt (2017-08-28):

Time: 29Jun17_1050
Tester: nr16874
Board: d880395f6c95
Address: 192.168.235.1:50001
Tests:
	Contact:	success
	UniqueID:	success
	DigitalI2C:	success
	PowerChips:	success
	Voltages:	success
	Currents:	success
	LM82Temp:	success
	InDetectorI2C:	warning
	Temperature:	success
	ADCControl:	success
	Analog0I2C:	success
	Analog1I2C:	success
	ClockSA:	success

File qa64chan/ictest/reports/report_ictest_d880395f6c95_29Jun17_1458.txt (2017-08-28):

Time: 29Jun17_1458
Tester: nr16874
Board: d880395f6c95
Address: 192.168.235.15:50001
Tests:
	Contact:	success
	UniqueID:	success
	DigitalI2C:	success
	PowerChips:	success
	Voltages:	success
	Currents:	success
	LM82Temp:	success
	InDetectorI2C:	warning
	Temperature:	success
	ADCControl:	success
	Analog0I2C:	success
	Analog1I2C:	success
	ClockSA:	success

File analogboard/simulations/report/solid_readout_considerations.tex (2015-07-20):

% Short write-up of ideas for SoLiD neutrino oscillation experiment 
% front-end readout
%
%%%%%%%%%%%%%%%%%%%%%%%%%%%%%%%%%%%%%%%%%
% Arsclassica Article
% LaTeX Template
% Version 1.1 (10/6/14)
%
% This template has been downloaded from:
% http://www.LaTeXTemplates.com
%
% Template author:
% Lorenzo Pantieri (http://www.lorenzopantieri.net) with extensive modifications by:
% Vel (vel@latextemplates.com)
%
% License:
% CC BY-NC-SA 3.0 (http://creativecommons.org/licenses/by-nc-sa/3.0/)
%
%%%%%%%%%%%%%%%%%%%%%%%%%%%%%%%%%%%%%%%%%
\documentclass[
12pt, % Main document font size
a4paper, % Paper type, use 'letterpaper' for US Letter paper
oneside, % One page layout (no page indentation)
%twoside, % Two page layout (page indentation for binding and different headers)
headinclude,footinclude, % Extra spacing for the header and footer
apacite
]{scrartcl}

\input{structure.tex} % Include the structure.tex file which specified the document structure and layout

%----------------------------------------------------------------------------------------
%	TITLE AND AUTHOR(S)
%----------------------------------------------------------------------------------------

\title{SoLi$\delta$ Analogue Front End} % The article title

\author{David Cussans\textsuperscript{1} \& Wim Beaumont\textsuperscript{2}} % The article author(s) - author affiliations need to be specified in the AUTHOR AFFILIATIONS block

\date{} % An optional date to appear under the author(s)

\begin{document}

%----------------------------------------------------------------------------------------
%	HEADERS
%----------------------------------------------------------------------------------------

%% \renewcommand{\sectionmark}[1]{\markright{\spacedlowsmallcaps{#1}}} % The header for all pages (oneside) or for even pages (twoside)
%\renewcommand{\subsectionmark}[1]{\markright{\thesubsection~#1}} % Uncomment when using the twoside option - this modifies the header on odd pages
%\lehead{\mbox{\llap{\small\thepage\kern1em\color{halfgray} \vline}\color{halfgray}\hspace{0.5em}\rightmark\hfil}} % The header style

\pagestyle{scrheadings} % Enable the headers specified in this block

%----------------------------------------------------------------------------------------
%	TABLE OF CONTENTS & LISTS OF FIGURES AND TABLES
%----------------------------------------------------------------------------------------

\maketitle % Print the title/author/date block

\setcounter{tocdepth}{2} % Set the depth of the table of contents to show sections and subsections only

\tableofcontents % Print the table of contents

\listoffigures % Print the list of figures

\listoftables % Print the list of tables
%----------------------------------------------------------------------------------------
%	ABSTRACT
%----------------------------------------------------------------------------------------

\section*{Abstract} % This section will not appear in the table of contents due to the star (\section*)

The design considerations for the front-end readout of the SoLiD neutrino detector are described. The readout chain from the photo-detector to a sampling ADC is described. Circuit simulations are presented, including shaping time, stability and noise.  A SiPMT photo-detector of gain O($10^6$) is assumed, but the circuit could be modified in a straight-forwards manner to accept a single-ended signal from a conventional PMT.

%----------------------------------------------------------------------------------------
%	AUTHOR AFFILIATIONS
%----------------------------------------------------------------------------------------

{\let\thefootnote\relax\footnotetext{\textsuperscript{1} \textit{University of Bristol, United Kingdom}}}

{\let\thefootnote\relax\footnotetext{\textsuperscript{2} \textit{University of Antwerpen, Netherlands}}}

%----------------------------------------------------------------------------------------

\newpage % Start the article content on the second page, remove this if you have a longer abstract that goes onto the second page

\section{Introduction}

The $\mathrm{SoLi}\delta$ neutrino oscillation experiment uses Silicon Photomultipliers ( SiPMT ) coupled to a amplifier/shaper circuit followed by a sampling ADC. The SiPMT has a gain of O($10^6$), similar to a conventional PMT.

SiPMT gain varies rapidly over-voltage ( the amount by which the bias voltage exceeds the break-down voltage). Since the break-down voltage varies between devices it is advantageous to be able to adjust the bias voltage applied to each SiPMT. Since the range of bias voltage adjustment is small O(1V) it is possible to reduce the cost of the bias system by using the SiPMT in a differential circuit using a high voltage bias O(10-100V) common to all SiPMT and individual low voltage trim voltages for each SiPMT. In addition all readily available High accuracy ( > 12 bits ) fast sampling ( > 10MHz ) ADCs use differential inputs. This suggests the use of a fully differential amplifier/shaper circuit (SiPMTs have been used in Particle Physics with differential readout, e.g. \cite{5688208}

\subsection{Circuit Schematic}

Figure~\vref{fig:ada4932_schematic_simplified} shows the circuit schematic for a possible amplifier/shaper together with the SiPMT at the input and the input filter for the ADC at the output.

\begin{figure}[tb]
\centering 
 
\caption[Simplified SoLiD amplifier/shaper]{Simplified schematic of an amplifier/shaper circuit for SoLiD. The schematic includes the SiPMT and the filter and biasing components on the ADC+FPGA readout board.} % The text in the square bracket is the caption for the list of figures while the text in the curly brackets is the figure caption
\label{fig:ada4932_schematic_simplified}
\end{figure}

\section{SiPMT Simulation}

In order to predict the affect of the SiPMT capacitance and resistance on the amplifier circuit a detailed simulation of the SiPMT is used. The active macro-cells ( the ones which ``fire'' ) are described by a switched voltage source across a capacitor. The voltage source is disconnected when the current flowing drops below a threshold value, simulating the quenching of the cell. Passive macrocosms are modelled by a resistor and capacitor network. Figure~\vref{fig:active_macrocell} show simplified schematics of the model for the active cells. The model is taken from work described elsewhere \cite{Marano20131}. The parameters in the model need to be matched to the SiPMT being considered. For these simulations parameters matching a Hamamatsu S10362-33-25c~\cite{Hamamatsu_s12572} are used.

For this simulation the SiPMT is run with an over-voltage of 3.5V resulting in a gain of $0.375 \times 10^6$.
\begin{figure}[tb]
\centering 
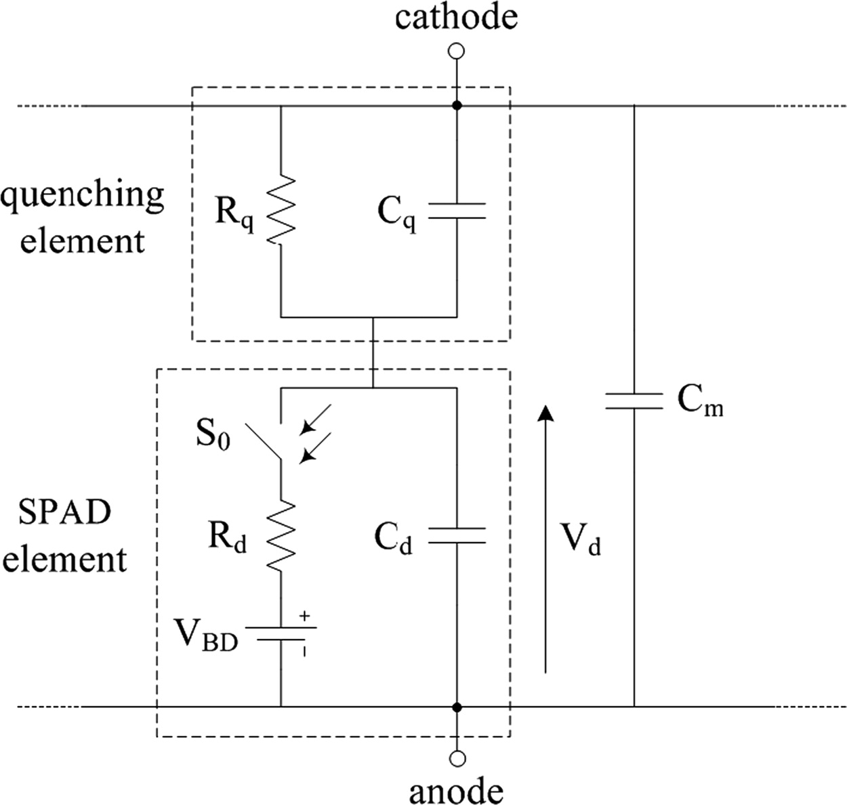
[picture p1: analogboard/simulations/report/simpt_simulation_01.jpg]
\subfloat[][Schematic of active cells. The cell firing corresponds to switch $S_0$ closing]{} 
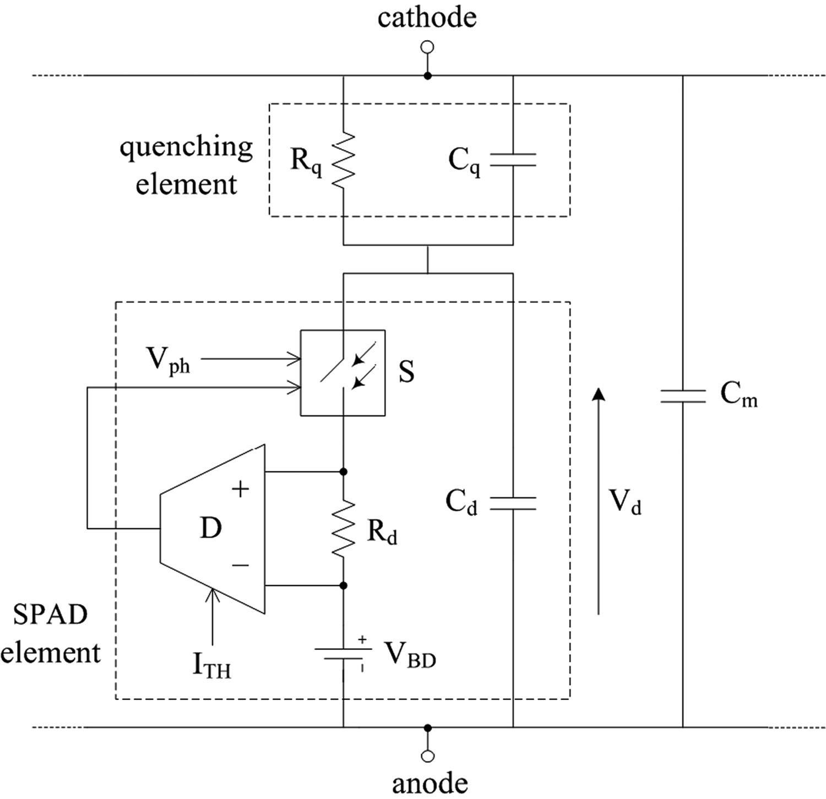
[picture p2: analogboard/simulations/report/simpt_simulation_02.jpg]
\subfloat[][Circuit including quenching]{} 
\caption[SiPMT simulation circuits]{Simplified schematic of a simulation for active cells in SiPMT (a), (b) includes switch for triggering pulse and quenching. An input pulse on $V_{ph}$ closes the switch which then opens when the current drops below $I_{th}$} 
\label{fig:active_macrocell}
\end{figure}

\section{Pulse Shaping}

The amplifier should take the signal from the SiPMT and produce a pulse optimized for sampling by the ADC+FPGA readout board. The amplifier shown in figure~\ref{fig:ada4932_schematic_simplified} has $\mathrm{CR}-(\mathrm{RC})^2-CR-RC$ shaping. The unusual configuration is dictated by the desire to AC couple the input from the SiPMT and the output to the ADC. $(\mathrm{RC})^2$ rather than $(\mathrm{RC})$ shaping was chosen to give a more symmetrical pulse (the fall time is only slightly longer than the rise time. reducing the total pulse width for a given pulse rise time).   

\subsection{Shaping Time}

This implies having enough samples on the rising edge of the pulse to accurately reconstruct pulse height and arrival time. The pulse shaping time should be as short as possible to reduce the amount of ``pile up'' from noise pulses. Optimization of the shaping time should be optimized based on the ADC sample rate, the analogue noise from the amplifier and the rate of ``dark noise'' pulses from the SiPMT. As a starting point an ADC sample rate of $40 \mathrm{MSamples/s}$ was chosen and a peaking time of $60\mathrm{ns}$. This is the sample sample rate/shaping time as chosen by the CMS ECAL\cite{1748-0221-5-03-T03011}.

An simulation of the pulse applied to the ADC inputs by the circuit shown in figure~\vref{fig:ada4932_schematic_simplified} in response to a 600 pixel avalanche pulse is shown in figure~\vref{fig:amplifier_600pa_response}

\begin{figure}[tb]
\centering 

\caption[Simulated signal at ADC input for one 600PA pulse]{Simulated signal at inverting and non-inverting ADC inputs in response to 600PA pulse.}
\label{fig:amplifier_600pa_response}
\end{figure}

\subsection{Unipolar/Bipolar}

Being able to use a low-voltage trim in combination with a single HV bias dictates AC coupling from the SiPMT in some form. Differential ADCs are a mid-scale when the two inputs are at the same voltage. Biasing the ADC so that zero input voltage corresponds to full scale gives one additional bit of dynamic range compared to zero input voltage giving the same voltage at the two ADC inputs. Biasing the ADC inputs in this way implies AC coupling.

If the amplifier is AC coupled a decision has to be made about whether to use unipolar or bipolar shaping. If unipolar shaping is used then if a large number of pulses are received at the input the baseline will drift since the integrated voltage must remain constant over a long time-scale. If bipolar shaping is chosen then the pulse area is zero over a short time-scale.

Bipolar shaping seems initially attractive, since high pulse rates will not result in baseline shift and so the trigger threshold will not need to be adjusted as a function of pulse rate. However in order to trigger on neutrons it is desirable to calculate the total area as well as the maximum amplitude of the pulses. Hence unipolar shaping is almost mandatory for SoLiD.

Figure~\ref{fig:amplifier_600pa_multipulse_response} shows the response of the amplifier to ten 600PA pulses in a period of $2\mu\mathrm{s}$. The baseline shifts by 17mV, corresponding to a shift of 19 pixel-avalanches. The baseline shift reduces to 14mV $2\mu\mathrm{s}$ after the end of the pulses.

\begin{figure}[tb]
\centering 

\caption[Simulated signal at ADC input for ten 600PA pulses]{Simulated signal at ADC input to ten 600PA pulses over a period of $2\mu\mathrm{s}$. The baseline shifts by an amount equivalent to a pulse height of 19PA.}
\label{fig:amplifier_600pa_multipulse_response}
\end{figure}

\subsection{Component Values}

Table~\vref{tab:component_values} lists the component values in the simulated circuit. A neutron light output time of $10\mu\mathrm{s}$ is assumed.

\begin{table}[tb]
\centering
\begin{tabularx}{\textwidth}{|l|l|X|} % Columntype Y declared in structure.tex
%\begin{tabular}{|l|l|l|} % Columntype Y declared in structure.tex
 Components & Value &  Comments \\
\toprule % from booktabs

$\mathrm{C}_\mathrm{ifp}$ , $\mathrm{C}_\mathrm{ifm}$ & $30\mathrm{nF}$ & Together with $\mathrm{R}_\mathrm{g}$ and the output impedance of the SiPMT forms a high-pass filter that blocks the DC bias to the SiPMT.  The RC time-constant should be larger than the neutron light output time.\\ \midrule

$\mathrm{R}_\mathrm{gp}$ , $\mathrm{R}_\mathrm{gm}$ & $50\Omega$ & Together with $\mathrm{C}_\mathrm{if}$ and the output impedance of the SiPMT forms a high-pass filter. Together with $\mathrm{R}_\mathrm{f}$ and  $\mathrm{C}_\mathrm{f}$ sets the gain of the amplifier. Sets the input impedance at medium frequency, so should be set to half the cable characteristic impedance.\\ \midrule

$\mathrm{C}_\mathrm{fp}$ , $\mathrm{C}_\mathrm{fm}$ &  $7.7\mathrm{nF}$ & Together with $\mathrm{R}_\mathrm{f}$ sets the gain and shaping time of the amplifier  \\ \midrule

$\mathrm{R}_\mathrm{fp}$ , $\mathrm{R}_\mathrm{fm}$ &  $2440\Omega$ & Together with $\mathrm{C}_\mathrm{f}$ sets the gain and shaping time of the amplifier  \\ \midrule

$\mathrm{R}_\mathrm{of1m}$ , $\mathrm{R}_\mathrm{of1p}$ &  $50\Omega$ & Together with $\mathrm{C}_\mathrm{of1}$ forms a RC low pass filter. Set $\mathrm{R}_\mathrm{of1}\mathrm{C}_\mathrm{of1}/2 = \mathrm{R}_\mathrm{f}\mathrm{C}_\mathrm{f}$. Also sets the output impedance at low frequency \\ \midrule

$\mathrm{C}_\mathrm{of1}$  &  $45\mathrm{pF}$ &  \\ \midrule

$\mathrm{C}_\mathrm{hpp}$ , $\mathrm{C}_\mathrm{hpm}$ &  $300\mathrm{nF}$ & Together with $\mathrm{R}_\mathrm{t}$ forms a high-pass filter that allows the DC bias to the ADC to be set. The RC time-constant should be larger than the neutron light output time. \\ \midrule

$\mathrm{R}_\mathrm{tp}$ , $\mathrm{R}_\mathrm{tm}$ &  $50\Omega$ & Sets the input impedance of the ADC at high frequency. \\ \midrule

$\mathrm{R}_\mathrm{of2m}$ , $\mathrm{R}_\mathrm{of2p}$ &  $100\Omega$ & Together with $\mathrm{C}_\mathrm{of2}$ forms a RC low pass filter. Set $\mathrm{R}_\mathrm{of2}\mathrm{C}_\mathrm{of2} = \mathrm{R}_\mathrm{f}\mathrm{C}_\mathrm{f}$. \\ \midrule

$\mathrm{C}_\mathrm{of2p}$ , $\mathrm{C}_\mathrm{of2m}$ &  $183\mathrm{pF}$ &  \\
\bottomrule

%\end{tabular}
\end{tabularx}
\caption{Component values for amplifier/shaper}
\label{tab:component_values}
\end{table}

\section{Cross-Talk between Channels}

Signals in one channel will induce signals in adjacent channels. The amount of cross talk is difficult to simulate but experience suggests it will probably be in the range 1 - 2 \% . Reducing cross talk is possible, but would require more time to perform PCB layout, increased number of interactions and more expensive connectors. This should be justified by simulation of the physics requirements.

\section{Input/Output Impedance}

In order to preserve maximum flexibility for location of the amplifier/shaper ( close to the SiPMT / close to the ADC / cables to both ) the input and output impedance should be matched to the characteristic impedance of a differential cable ( typically $100\Omega$ ). 
 
\section{Noise Requirements}

The dynamic range for the amplifier is set by wanting to be able to measure signals as small as one pixel avalanche ( in order to calibrate the SiPMT gain ) and as large as five times the most probable energy deposit from a cosmic ray muon in order to calibrate the light output from the cubes. In SM1, five times the most probable energy deposit from a cosmic ray muon corresponds to approximately 600 PA~\cite{ref:cosmic_calibration}

Full scale differential voltage range of the ADC is $1-2\mathrm{V}$ ( i.e. the voltage swing of each input is $0.5-1\mathrm{V}$). If a differential voltage range of 1V and a full scale of 600PA is assumed this corresponds to differential voltage of $1.7\mathrm{mV}/\mathrm{PA}$, or voltage of $850\mu\mathrm{V}/\mathrm{PA}$ at each ADC input for each pixel avalanche. If it is desired to have 10 ADC counts per PA this implies $85\mu\mathrm{V}/\mathrm{count}$. Ideally the RMS noise should be less than one ADC count.

\subsection{Noise Simulation}

Figure~\vref{fig:noise_simulation} shows the simulated output
noise. The thermal noise of the resistors and most of the noise
sources inside the Op-amp are simulated. Integrated between 100Hz and
1GHz the simulation predicts an RMS noise at each ADC input of
$28\mu\mathrm{V}$ , comfortably below the target of
$85\mu\mathrm{V}$. In fact the effect of this noise would be even lower, since several samples would be summed to estimate the charge in a pulse. However, it should be emphasized that the
simulation only includes internally generated noise from the amplifier
circuit, it does not include the effect of external noise picked up on
cables etc.

\begin{figure}[tb]
\centering 

\caption[Simulated output noise at  ADC input]{Simulated noise at  ADC input. Thermal noise from resistors and most sources of noise inside the op-amp are included.}
\label{fig:noise_simulation}
\end{figure}

\section{Amplifier Choice/Stability Considerations}

The amplifier/shaper needs to be stable at all frequencies. One way of verifying this in simulation is to simulate the open loop gain. In an ideal inverting amplifier circuit, if the feedback loop between the amplifier output and input is broken and a voltage applied to the inputs an infinite signal is generated at the circuit node that was connected to the input before the loop was opened. This signal is $180^\circ$ out of phase with the input signal. Hence, when the loop is closed this feedback ensures that the input is always a ``ground''. A real ( non-ideal ) amplifier has finite gain and a non-zero phase-shift, both of which vary with frequency. If the feedback components, or the amplifier, are badly chosen the open-loop phase shift can drop to $0^\circ$ at a frequency where the gain is > 1 and the circuit will oscillate. A ``rule of thumb'' is that the phase shift should not drop below $45^\circ$ at any frequency where the amplifier gain is greater than unity (i.e.. the phase margin should be greater than $45^\circ$ ).

The operational amplifier should be chosen so that the bandwidth is high enough that the pulse shape depends almost entirely on the passive components in the feedback network but should also have gain/phase characteristics that ensure the amplifier is stable.

Figure~\vref{fig:phase_margin} shows the open-loop gain for the circuit shown in figure~\ref{fig:ada4932_schematic_simplified} with two different amplifiers, the Analogue Devices ADA4932 and the Linear Technologies LTC6404-4. The bandwidth of the ADA4932 is only just sufficent for the circuit but it gives a phase margin of $48^\circ$. The LTC6404-4 has a higher bandwidth but gives a phase margin of  $24^\circ$ which is likely to result in an amplifier/shaper that oscillates or ``rings'' in response to pulses.

\begin{figure}[tb]
\centering 
\subfloat[][Open Loop Gain with LTC6404-4]{} 
\subfloat[][Open Loop Gain with ADC4932]{} 
\caption[Closed loop gain with different Op-amps]{Open loop gain for amplifier shaper for (a) LTC6404-4 with a phase margin of $24^\circ$ and (b) ADA4932 with a phase margin of $48^\circ$} 
\label{fig:phase_margin}
\end{figure}

%\renewcommand{\refname}{\spacedlowsmallcaps{References}} % For modifying the bibliography heading

\bibliographystyle{unsrturl}

\bibliography{solid_sipmt.bib} % The file containing the bibliography

%----------------------------------------------------------------------------------------

\end{document}

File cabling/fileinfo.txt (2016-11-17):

dir SiPm   : SiPm ribbon cable 
dir img :  svg files used for the initial cable files
dir initialcablestudies  : calculation inital made to estimate the cable diameters with LV power units outside the container

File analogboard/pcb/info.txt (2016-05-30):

directory description 
SOL_AMP2  : directory with original 8 ch proto type design files and sub dir data sheets 
SOL_AMP2_1_DC  : directory with the patch documentation to get the DC information
SOL_AMP2_1_DC/brdinfo  :  files with the individual board information /results

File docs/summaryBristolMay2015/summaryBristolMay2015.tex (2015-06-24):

\documentclass[a4paper]{article}

\RequirePackage{graphicx}
\usepackage{authblk}
\usepackage{cleveref}
\usepackage{caption}
%\usepackage{subcaption}
\usepackage[UKenglish]{babel}
\usepackage{alltt}
\usepackage{afterpage}
\usepackage[text={16cm,25cm},centering]{geometry}

%\geometry{
%  a4paper,%
%  top=3cm,%
%  textwidth=16cm,% 
%  textheight=23.2cm,%
%  marginparsep=7pt,% 
%  marginparwidth=2.5cm%
%}

\renewcommand*{\familydefault}{\sfdefault}

\title{Summary of 18th/19th May 2015 Readout System Meeting in Bristol}
\author[1]{Wim Beaumont}
\author[2]{David Cussans}
\author[2]{David Newbold}
\author[3]{Nick Ryder}
\author[3]{Alfons Weber}
\affil[1]{Universiteit Antwerpen}
\affil[2]{University of Bristol}
\affil[3]{University of Oxford}

\date{\today\\V0.0}

\begin{document}

\maketitle

\abstract{
A meeting was held on the 18th/19th of May, 2015, to discuss the readout design for the full SoLid detector.
A proposal for a system level design was agreed.
A number of options for detector parameters were identified.
The collaboration will have to decide on certain parameters soon.
The impact that these decisions will have on the readout system are explained.
A plan for the readout system development is proposed.
}

\tableofcontents

\section{System level design}

A modular system design was chosen to separate development tasks.
An overview of the system design is shown in \cref{systemoverview}.
More detail on each part of the system is given in the following sections.

\begin{figure}[htp]
    \begin{center}
        
        \caption{Overview of the system level readout design.}
        \label{systemoverview}
    \end{center}
\end{figure}

As with SM1 each SiPM sensor will be on its own small PCB, held in contact with the wavelength shifting fibre.

Multiple sensor boards will be connected to each analog board.
The analog boards will bias the sensor and amplify the signals from avalanches in the detector.
The sensor will be connected to the analog board by a small twisted pair cable.
The high voltage bias will be provided by a bench top supply, with bias control for each channel provided by modifying the sensor's low voltage using a DAC.
The multi channel DAC will be controlled via an I$^2$C bus, which will also allow communication with a unique ID chip.

Potentially multiple analog boards will then connect to each digital board.
Depending on the proximity between the analog board(s) and the digital board different connections may be used, either an edge connector or a ribbon of cables.
The digital boards will digitise the amplified analog signals, buffer the signal data and make local trigger decisions.
The signals will be digitised in 40 MS/s, 14 bit ADCs.
An Artix 7 family FPGA, housed on a commercial board providing power, clock oscillators, etc.
The digital board will also have an I$^2$C bus that can be controlled via the FPGA, as well as a unique ID chip.
The digital boards will be able to communicate with each other and over the network via fast links.

The computing for the system is expected to be commodity PCs.
They will receive the slow control and waveform data.
The software will perform data reduction on the triggered data before writing it to disk.
The computing system will act as a short term (few day) cache of the data, which will be transferred off site for long term storage.

The system is designed to ensure modularity, potentially down to the plane level.
This will allow either each plane or a small number of planes, to be run independently.
This will allow, for example, pre-deployment tests with radioactive sources and cosmic rays using the full read-out chain for a plane.
The modularity will also allow flexibility in the grounding scheme used, giving the potential to fully isolate each plane from the others if needed.

The layout of the system parts was also considered.
Assuming single ended read-out of the fibres, the preferred layout would be to place all SiPMs on two adjacent edges of the detector.
From here all cables would be routed to the shared corner, out of the plane and to the analog and digital board which would be mounted outside the shielding within the footprint of the plane.
The cabling for the sensors may be a small number of ribbon cables per edge, allowing simple connection to the analog boards.
The shielding of the detector should be designed such that the analog and digital boards do not need to be removed from their mounting to access the detector inside the shielding.

\section{Sensor choice}

To reduce the R\&D required in the upgrade it was decided to stay with $3\times3$ mm SiPMs.
It was noted that a 64 channel multi anode PMT may have a similar cost as the SiPMs, with better performance with regards to dark count, etc.
However, the R\&D work required to bring the fibres from multiple channels to a single PMT would be considerable.

A range of SiPMs should be considered for the upgraded system.
The three main options being:
\begin{itemize}
    \item Hamamatsu S12752-050P, the sensors used in SM1
    \item Hamamatsu's next generation $3\times3$ mm sensors with reduced cross talk
    \item Sensl's C series $3\times3$ mm sensors
\end{itemize}

Comparing the specifications of the sensors it seems that Sensl's C series may be a better replacement for the Hamamatsu sensors.
However, direct comparisons between the devices based on specifications is not easy, and so samples of the above sensors should be evaluated.
The evaluation should measure the gain, dark count rate and cross talk probability for each sensor for a range of temperatures and over voltages.

\section{Amplification and shaping}

It was decided that to minimise the noise the analog board should have minimal switching or digital electronics.
An external power supply should therefore be used, and the digital part of the board restricted to an I$^2$C bus that will be used infrequently.
A baseline amplifier circuit using a differential to differential amplifier, with low gain was selected.
This circuit is shown in \cref{amplifiercircuit}.
This board will be prototyped as a high priority, and tested using an oscilloscope before the digital board is ready.

\begin{figure}[htp]
    \begin{center}
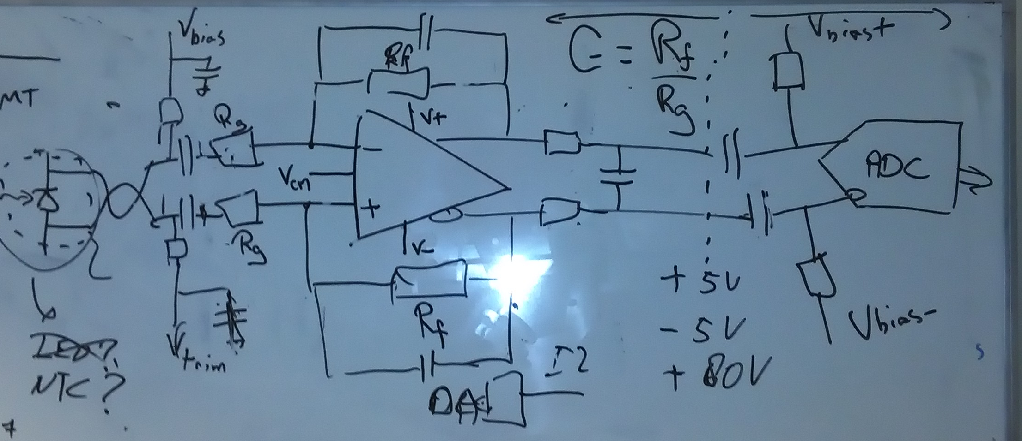
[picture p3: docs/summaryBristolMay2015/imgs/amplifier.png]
        
        \caption{Baseline amplifier circuit design.}
        \label{amplifiercircuit}
    \end{center}
\end{figure}

\section{Digitisation}

It was decided that reducing the current ADC sampling rate to 40 MS/s would simplify the data deserialisation and ease the requirements on the FPGA.
The single pixel avalanche will be targeted at roughly 10 ADC counts.
We will require measurements of up to 500 pixel avalanches.
The required resolution of the ADC will therefore be 14 bits.

A number of 40 MS/s, 14 bit ADCs are available on the market.
It is expected that they will be 4 or 8 channels per ADC chip, and that the price per channel will be reduced somewhat compared to the ADC used in SM1.
The different options available on the market will be evaluated so that a selection could be made in the near future.
It is hoped that an ADC with I$^2$C or something that is recognisable as SPI will be used.

\section{Firmware based trigger}

The trigger strategy for SoLid involves two levels in the FPGA.
First, the waveform from each channel will be zero suppressed to keep, if possible, all avalanches.
The zero suppression will require a method, such as a vertical/horizontal coincidence, to reduce the impact of the high dark count rate of the SiPMs.
The zero suppressed data from each channel will be stored in a ring buffer in a single RAM block in the FPGA.

Each waveform will also be analysed to provide a decision on multiple triggers.
As a minimum both a muon trigger (based on a high threshold) and a neutron trigger (based on a low amplitude, high integral signal).
These trigger decisions will be taken on plane by plane basis.
Following a trigger the buffered data from suitable time windows in a volume of the detector will be read out.
The time window for a muon trigger should be short, for example 10 samples, as only coincident signals will be required to reconstruct the muon.
The time window for the neutron trigger will be required to be up to 500 $\mu$s, so that an IBD analysis can be performed.
The time window and size of the RAM blocks places some constraints on the signal rate, described in detail in \cref{maxrates}.

The Artix 7 family of FPGAs was selected as a price optimised range expected to have sufficient resources for our needs.
The choice of FPGA within this family will be made based on the number of channels expected to be read using each digital board.
The trigger design will require that a whole plane be triggered in a single FPGA, while it may be possible for multiple planes to use the share an FPGA.

Each FPGA will make trigger decisions that will be propagated to the other digital boards in a token ring system.
This will allow channels in neighbouring planes to be read out based on a trigger in another plane.
Each digital board will therefore require one or two data links to pass information to its neighbours as well a an ethernet link for transmitting data to the computing system.
Depending on the locations of each board it may be possible to use low cost links between the board.
The Artix 7 FPGAs are capable of using 3.2 Gb/s tranceivers, placing a limit on the data passed between boards to something like 64 bit.
This will allow a trigger decision to be passed to a few neighbouring planes per sample.

To reduce the latency in transferring the data from the FPGAs to the PCs an upcoming IPbus upgrade will be used.
This upgrade will automatically push data over the network, rather than relying on the software to poll for buffered data before starting a transfer.

\subsection{Maximum signal rate for zero suppression}
\label{maxrates}

Each channel's buffer for the zero suppressed data must fit within a single 4608 byte RAM block.
It is assumed that 24 bytes will be stored for each significant EM signal: 4 bytes for timing information and 10 samples each requiring 2 bytes.
A neutron signal will store timing information and 100 samples, requiring 104 bytes.
Each buffer must be able to store a neutron signal and as many significant signals as are needed to contain the IBD analysis time window of $500 \mu$s.
The size of the RAM block ($S_b$) therefore puts a limit on the rate of significant signals, $R_s$
\begin{eqnarray}
    S_b &\ge& S_n + \Delta t_{IBD}\times R_s \times S_s \\
    R_s &\le& (S_b - S_n) / (\Delta t_{IBD} \times S_s)\\
    R_s &\le& 375\mbox{ kHz}
\end{eqnarray}

Since the signal rate in fact fluctuates a safety margin is needed to ensure that all required signals will still be in the buffer at the time of a trigger, and so a target rate of $R_s = 200$ kHz is required.

The aim of the readout system will be to keep all signals from the SiPMs in the zero suppressed buffer, ie using a zero suppression threshold below a single pixel avalanche level.

At low thresholds the dominating signal seen by the SiPMs comes from the high dark count rate.
For the S12572-050C MPPCs used in SM1 the dark count rate (for single pixel avalanches, at $25^{\circ}$C) is typically 1 MHz and maximally 2 MHz.
Other sensors have lower dark count rates, although generally they are above the 200 kHz target rate.
The dark count can also give multi pixel avalanches due to the cross talk between pixels, which ranges from 5\% to 45 \% depending upon the over voltage.
The dark count rate at a level of $n$ photons can be approximated as
\begin{equation}
    R_d(n) = R_d(0)\times C^n,
\end{equation}
with a cross talk probability of $C$.

A range of techniques are available for reducing the signal rate due to dark counts.
The simplest method is to raise the zero suppression threshold.
The firmware will have a programmable zero suppression threshold that can be set at run time.
However this option both reduces the dark count rate and also loses low intensity physical signals, such as those from 511 keV positron annihilation $\gamma$s.

Another method to reduce the signal rate due to dark counts is to require a coincidence between multiple sensors.
In a detector design with a single sensor per row of scintillator cubes a coincidence between at least one vertical and at least one horizontal row can be made.
The signals due to dark counts are then reduced to the rate of accidental coincidences between a vertical and a horizontal row, while real scintillation signals are expected to always give a signal on horizontal and vertical fibres.
The coincidence rate can be estimated as the produce of the signals in each sensor, the time window of the coincidence ($\Delta t$) and the number of sensors compared in the coincidence, $n_{SiPM}$.
\begin{equation}
    R_d^{coinc}(n) = (R_d(0)\times C^n)^2\times\Delta t\times n_{SiPM}
\end{equation}
For the full scale SoLid experiment two possible detector dimensions are being considered: $n_{SiPM} = 16$ or $24$.

If the number of sensors per row of cubes is doubled (either by having a SiPM at either end of a single fibre, or two fibres each with a single SiPM) then a coincidence can be required only with the other SiPM in the same row, reducing $n_{SiPM}$ to 1 and giving a more powerful signal rate reduction.

The signal rates in different scenarios can be estimated in order to select a design that sufficiently lowers the signal rate.
\Cref{rates_s12572_30pct} shows the estimated signal rates using the S12572 MPPC with the over voltage suggested by Hamamatsu, which has a 30\% cross talk probability, and operating at $25^{\circ}$C.
The estimated rates are shown as function of the zero suppression threshold and for different coincidence requirements, either no coincidence, or coincidence with $n_{SiPM} = 1, 16\mbox{ or }24.$
At this over voltage and temperature the required rate can only be achieved with a 0.5 PA threshold using multiple SiPMs per row of scintillator cubes.
In a single ended readout scheme a threshold of 2.5 PA is required to sufficiently reduce the dark count rate.

\begin{figure}[htp]
    \begin{center}
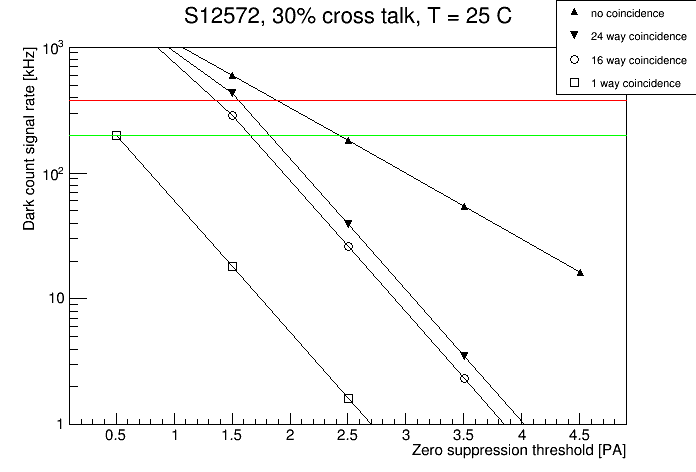
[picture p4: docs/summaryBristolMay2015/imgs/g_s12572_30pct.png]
        
        \caption{Estimated signal rates for the S12572 MPPC operated with a 30\% cross talk probability.}
        \label{rates_s12572_30pct}
    \end{center}
\end{figure}

Operating the S12572 at a lower over voltage reduces the cross talk probability.
As shown in \cref{rates_s12572_10pct}, operating with an over voltage that reduces the cross talk to 10\% in a single ended readout scheme can allow a 1.5 PA threshold to sufficiently reduce the signal rate.

\begin{figure}[htp]
    \begin{center}
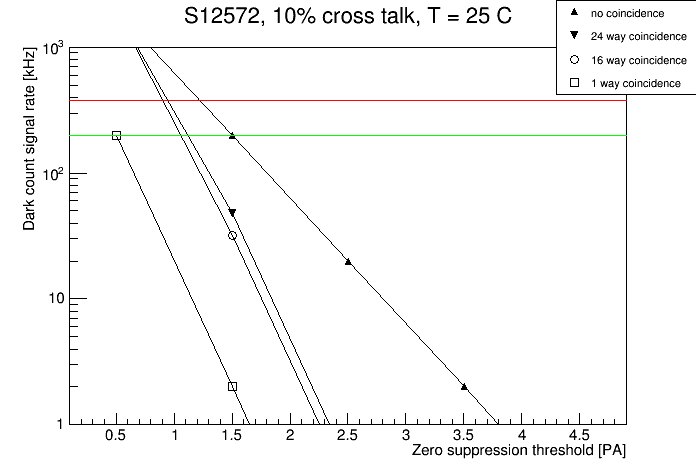
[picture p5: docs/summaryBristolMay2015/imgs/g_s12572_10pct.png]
        
        \caption{Estimated signal rates for the S12572 MPPC operated with a 10\% cross talk probability.}
        \label{rates_s12572_10pct}
    \end{center}
\end{figure}

The sensl SiPMs may have a reduced dark count rate.
The estimated signal rates for a C Series SiPM are shown in \cref{rates_sensl_10pct}, operating with a 10\% cross talk probability at $21^{\circ}$C.
Again, a threshold of 1.5 PA is required in a single ended readout scheme.

\begin{figure}[htp]
    \begin{center}
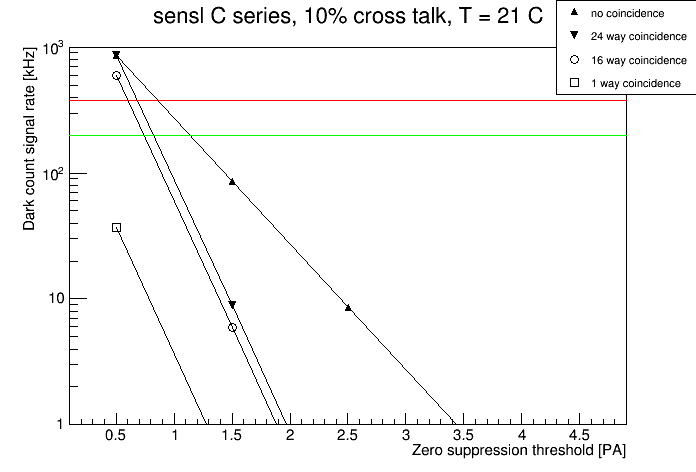
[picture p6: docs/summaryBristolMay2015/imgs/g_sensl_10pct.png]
        
        \caption{Estimated signal rates for the Sensl C series SiPM operated with a 10\% cross talk probability.}
        \label{rates_sensl_10pct}
    \end{center}
\end{figure}

The dark count rate of a SiPM is highly dependant upon the temperature of operation.
By cooling the sensors the rate can be reduced, leading to a dramatic reduction in the coincidence rate.
\Cref{rates_s12572_10pct_5C} shows the reduction in estimated rates by cooling the S12572 MPPC to $5^{\circ}$C, allowing a 0.5 PA threshold even with a $24\times24$ cube system with single ended readout.
Cooling the SiPMs would require changes to the mechanical design of the detector, but would allow zero suppression with no loss of scintillation signals without the additional cost of doubling the number of sensors per detector volume.

\begin{figure}[htp]
    \begin{center}
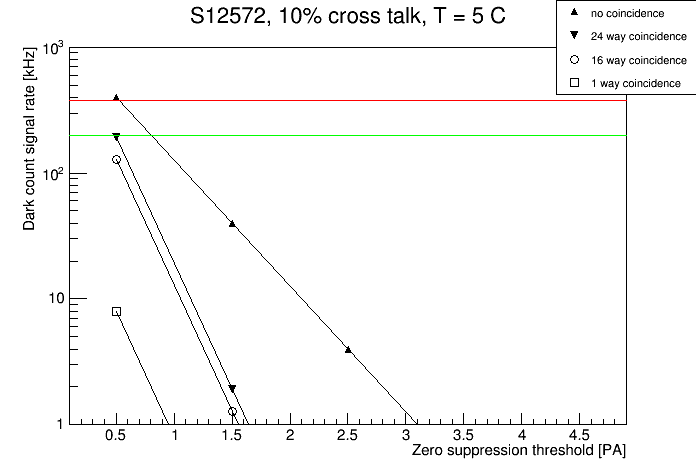
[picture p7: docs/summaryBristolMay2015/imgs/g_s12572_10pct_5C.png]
        
        \caption{Estimated signal rates for the S12572 MPPC operated with a 10\% cross talk probability cooled to $5^{\circ}$C.}
        \label{rates_s12572_10pct_5C}
    \end{center}
\end{figure}

In order to meet the required signal rate there are therefore three options available:
\begin{enumerate}
    \item Increase the zero suppression threshold at the cost of losing small amplitude signals such as annihilation gammas
    \item Increase the number of sensors per row of cubes, at the cost of roughly doubling the readout system cost (and possibly doubling the fibre cost)
    \item Reduce the temperature of the system to approximately 5$^{\circ}$C, at the cost of complicating the mechanical design and operation
\end{enumerate}

\section{Software based data reduction}

The quantity of data written to disk should be reduced to the quantity that can be transferred out of SCK over the network.
This will require data reduction in software of the triggered data.
The main strategy will be to look for time coincident signals in different locations of the detector, and remove any signals with low amplitude that are not time coincident with a larger amplitude signal.
This will require more processing power than the SM1 DAQ software, which simply writes data to disk.

As the data strategy is to only keep a few day cache of the data on site, it will also mean that a large disk server will not be required.
The system should therefore be capable of running in a small number of commodity PCs, some of which will have a few TB of data storage to use as the local cache.

\section{Slow control}

The preferred communication method for all slow control is via I$^2$C busses.
The communication for different parts of the system may be through the readout FPGAs or microcontrollers.
Each board, set of sensors or physical plane should have a unique ID chip associated, to avoid ambiguity in the slow control system.

In addition to the bias control DACs, the main slow control element will be temperature sensors, which will be on separate I$^2$C busses, probably communicating via microcontrollers over ethernet.
If the choice is made to cool or temperature control the detector then the slow control system will also have to control the cooling systems.

\section{Readout system development plan}

The design of the system is such that there are multiple development streams that are not strongly coupled.
An initial timescale for these tasks is given in \cref{plan}.

\begin{table}[htp]
    \begin{center}
        \caption{Development plan}
        \label{plan}
        \begin{tabular}{p{0.25\textwidth}p{0.75\textwidth}}
            \hline
            \hline
            Date & Tasks \\
            \hline
            Jun 15 - Sep 15 & 
            \begin{itemize}
                \item Characterise and select SiPM
                \item Identify ADC
                \item Prototype analog board design
                \item Prototype digital board design
                \item Firmware tests
                \item Software tests
            \end{itemize}
            \\
            Sep 15 - Jan 16 & 
            \begin{itemize}
                \item Produce, test with oscilloscope and redesign analog board 
                \item Prototype digital board design and production
                \item Implement prototype software
                \item Implement prototype firmware
                \item Software design
                \item Firmware design
            \end{itemize}
            \\
            Jan 16 - Apr 16 & 
            \begin{itemize}
                \item Test analog board with prototype digital board
                \item Finalise analog design
                \item Finalise digital design
                \item Implement production firmware
                \item Implement production software
            \end{itemize}
            \\
            Apr 16 - Jul 16 & 
            \begin{itemize}
                \item Produce modules 1 - 3 boards
                \item Test module 1
            \end{itemize}
            \\
            Jul 16 - Oct 16 & 
            \begin{itemize}
                \item Deploy module 1
                \item Debug firmware
                \item Debug software
                \item Test module 2
                \item Deploy module 2
                \item Test module 3
            \end{itemize}
            \\
            Oct 16 - Jan 17 & 
            \begin{itemize}
                \item Deploy module 3
            \end{itemize}
            \\
            \hline
            \hline
        \end{tabular}
    \end{center}
\end{table}

\section{Input needed from collaboration}

A number of decisions have to be made about the full scale detector in the near future:
\begin{itemize}
    \item The number of cubes per plane
    \item The choice between increasing the number of sensors, increasing the zero suppression threshold or decreasing the temperature of the system
\end{itemize}

\end{document}

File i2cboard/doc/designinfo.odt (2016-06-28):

## Choice LDO's

The 3.3V ON LDO's are small and cheap. Still can be controlled.

150mA should be sufficient to drive a number of external I2C devices that have for standard operations currents << 10mA

The maximal voltage for these LDO's are 5.5 V ( operational voltage, 6V absolute max )

To get some margin a 1N4448 ( 500mA ) is placed in front of all the LDO's

expected current < 300mA , .3 * 1.5 = .450 mW

need 1uF at the ouput / input

### Temperature allert .

The enable input of U1 is connected to the temperature allert output of the AT30TSE752. This is done via a resistor so the function can be "removed",

## I2C circuits

### PCA9517A buffer: (obsolete)

Was a consideration for only 2 I2C busses.

If the power on the external buffer is switched off the I2C lines will pull down and it will not be possible to control the MCP23009.

It is important that the LDO's and the I2C buffers are controlled by the same line, both high.

The PCA9571 can only drive 400pF. Consider to use in series a 82B715D bus extender.
But the 82B715D has no disable function. Didn't find a device that can do both.

PCA9515 was also considered as this has only one power supply but is an "old" device .

Check if the PCA9571 to replace the level shifter on the analogue board.

### P82B715

With V 0.4 it is assumed there are three I2C busses on X1.

The SCL_L is used to control the devicies on the card.

SCL1in and SCL2in are the busses to communicate with the remote sensors.
If the power supply on these remote sensors are off , the SCLXin , SDAXin lines will be pulled to zero. The "master" that controls these lines should be able to cope with this.

The P82B715 is able to drive a high capacitive load on its LX and LY outputs but has no disable function.

other option would be TCA4311A or PCA9510A. But these can only drive 400pF altough intended to drive a back plane. These support hot swappable what is what we do.

## PCA9557

pin assignment is not yet fixed. Depends on the layout.

Only IO0 will be fixed to GPIO as this is an open drain. There is a pull up resistor R9

# Programming ID

R10 and R11 are there to make it possible to lock and unlock the AT30TSE752 flash. This should contain ID information about this board. Connections have to be made via TP0 and TP1 these have a kind of press fit for std pin headers ( square pins)

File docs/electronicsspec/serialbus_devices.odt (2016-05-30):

Serial interfaces SOLID

version 0.1

last modified date : May 30, 2016

# I2C devices on the analogue board

The analogue board has two independent I2C buses.

Bus 1 and bus 2.

For normal operations the

### devices om I2C bus 1

Device | ref nr | "fix address" | address | address ( "8 bits") | set by | manfr device
DAC bias | u4 | 110000x | 1100001 | C1 | resistor high | MCP4725A0
DAC trim1 | u1 | 1100PPP | 1100100 | C4 | pcb test | MCP4728
DAC trim2 | u2 | 1100PPP | 1100101 | C5 | pcb test | MCP4728
DAC trim3 | U6 | 1100PPP | 1100110 | C6 | pcb test | MCP4728
DAC trim4 | U7 | 1100PPP | 1100111 | C7 | pcb test | MCP4728
IO general | | 0100xxx | '0100000 | 80 | resistor gnd | MCP23009

Functional description

- DAC bias single channel Set the bias for the board. startup output voltage can be programmed. The base address 1100MMx where M is defined is set during manufacturing. As default the version where MM is set to 00 is ordered. ( MCP4725A0 <-- ) link to data sheet readout-system\analogboard\pcb\SOL_AMP2\datasheets\MCP4725_1470577.pdf
- DAC trimX Quad channel DAC The base address 1100PPP The sub addresses PPP are set during the PCB test procedure. Eventual address can be different from the table above. To be verified in the test report of the board. Set the trim voltages for a group of 4 input channels readout-system\analogboard\pcb\SOL_AMP2\datasheets\MPC4728.pdf
- IO general purpose General purpose IO device. This device is used to switch on the LV power supplies of the board and to enable the on board I2C devices. This device is powered from an external 3.3V ( via the DIN The address is set via a analogue level. The address pin is set to gnd so effectively set to sub address 0. readout-system\analogboard\pcb\SOL_AMP3\doc\MCP23009

### Devices on I2C bus 2

Device | ref nr | "fix address" | address | address ( "8 bits") | set by | manfr device
DAC trim5 | | 1100PPP | 1100100 | C4 | pcb test | MCP4728
DAC trim6 | | 1100PPP | 1100101 | C5 | pcb test | MCP4728
DAC trim7 | | 1100PPP | 1100110 | C6 | pcb test | MCP4728
DAC trim8 | | 1100PPP | 1100111 | C7 | pcb test | MCP4728
temp sens ID EEPROM sw write prot general call | | 1010xxx 1001xxx 0110xxx 0000000 | 1010000 1001000 0110000 0000000 | A0 90 60 00 | resistors | AT30TSE752A

- DAC trim X see bus 1
- temperature sensor ID sensor details see external sensors Sensor can read temperature and has an EEPROM. EEPROM will be programmed and locked during analogue board assembly . very cheap.

# I2C devices on the I2C interface board and external cables

## Sensirion SHT21

details see external sensors

connected to the external I2C 1bus.

Not located on an "active" board to limit the heating up via the PCB.

## External I2C bus

The external I2C bus will be connected to temperature sensors and eventual temperature sensors.

The bus will be powered off most of the time

electrical characteristics:

cable resistance ~ .2 ohm/m

Voltage : nominal 3.4 V voltage drop estimate 2x .07 @ 100mA

current : max 100mA , ( 10 mA / device)

max lenght cable 3.5m

4 wires

wire | function
1 | Vdd
2 | SCL
3 | SDA
4 | GND

I2C :

pullup resistor 2.7 K at the source

max frequency 100 kHz ( to be confirmed)

## External sensors

## temperature ( and ID)
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

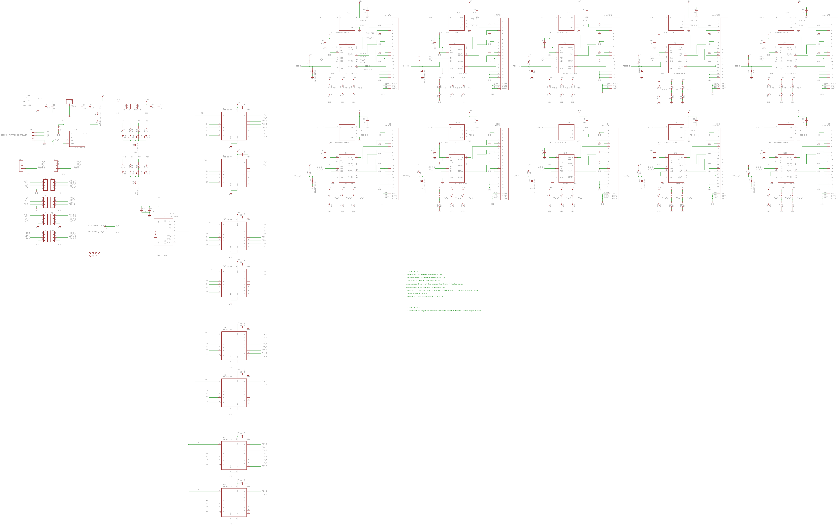
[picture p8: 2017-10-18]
jtagboard/schematic.png

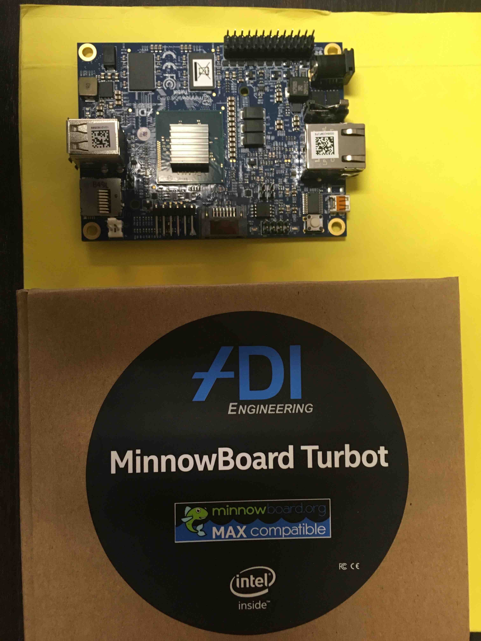
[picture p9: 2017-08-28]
docs/systemDescription/images/MinnowBoard.jpg

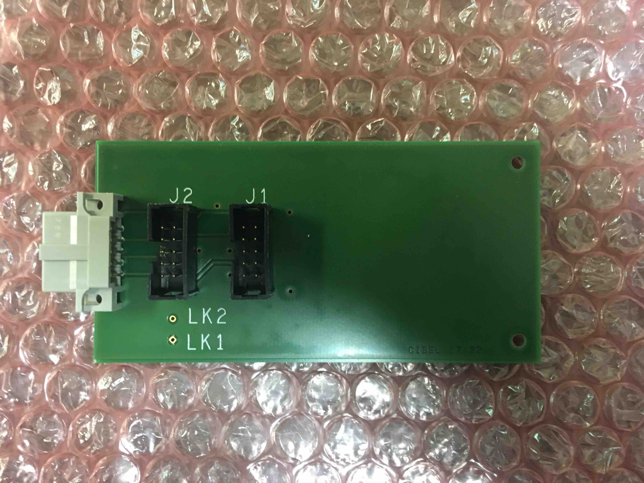
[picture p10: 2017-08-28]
docs/systemDescription/images/I2C_fanout.jpg

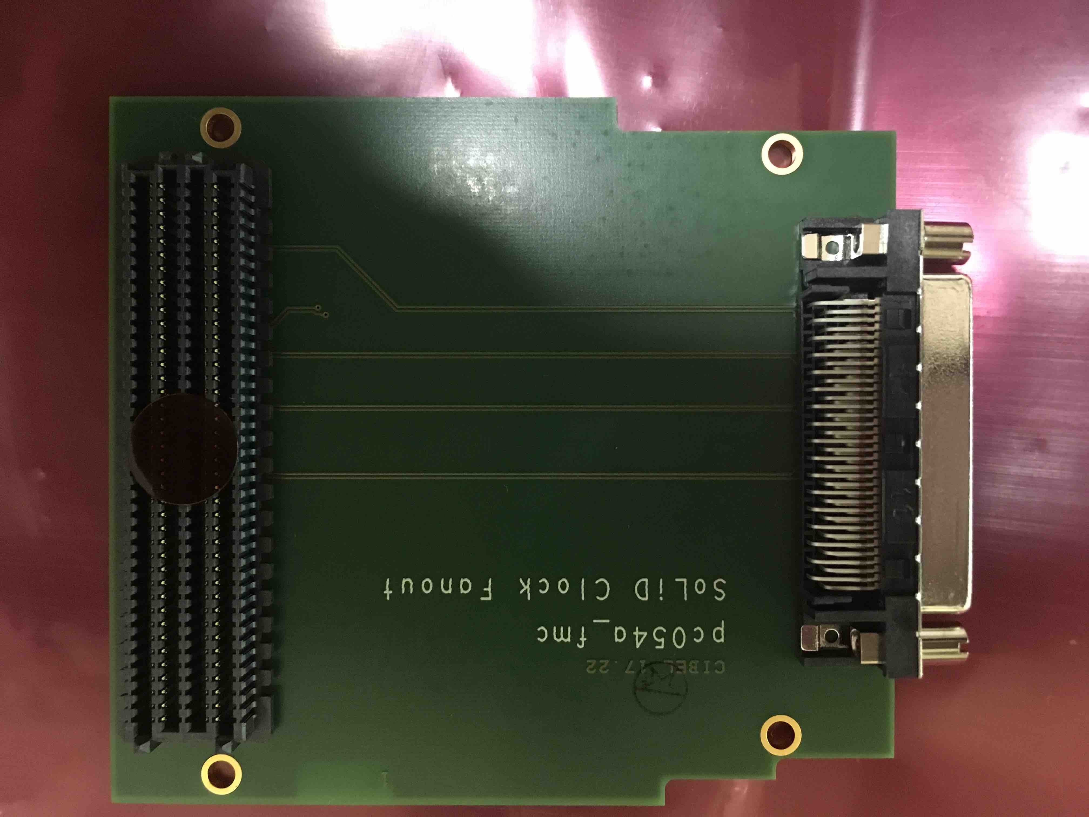
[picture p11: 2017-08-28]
docs/systemDescription/images/pc054a_fmc.jpg

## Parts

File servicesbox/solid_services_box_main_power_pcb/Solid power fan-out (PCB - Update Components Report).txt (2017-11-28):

Update Components Report
------------------------

Report File:        H:\Projects\SoLid\DCDC Test circuit\Solid Power Fanout\Solid power fan-out (PCB - Update Components Report).txt
Report Written:     Friday, October 28, 2016
Project Path:       H:\Projects\SoLid\DCDC Test circuit\Solid Power Fanout\Solid power fanout.prj
Design Path:        H:\Projects\SoLid\DCDC Test circuit\Solid Power Fanout\Solid power fan-out.pcb
Design Title:       
Created:            20/09/2016 08:58:07
Last Saved:         28/10/2016 14:59:54
Editing Time:       14537 min
Units:              mm (precision 1)

Library Files:
==============

C:\Users\Public\Documents\DesignSpark PCB\DownloadedLibrary\Connectors-PCB Connectors-PCB Headers.cml
C:\Users\Public\Documents\DesignSpark PCB\DownloadedLibrary\Connectors-PCB Connectors-PCB Terminal Blocks.cml
C:\Users\Public\Documents\DesignSpark PCB\DownloadedLibrary\DCDC convertors.cml
C:\Users\Public\Documents\DesignSpark PCB\DownloadedLibrary\Displays & Optoelectronics-LEDs & LED Accessories-Visible LEDs.cml
C:\Users\Public\Documents\DesignSpark PCB\DownloadedLibrary\Operational Amplifiers.cml
C:\Users\Public\Documents\DesignSpark PCB\DownloadedLibrary\Passive Components-Capacitors-Aluminium Capacitors.cml
C:\Users\Public\Documents\DesignSpark PCB\DownloadedLibrary\Passive Components-Capacitors-Ceramic Multilayer Capacitors.cml
C:\Users\Public\Documents\DesignSpark PCB\DownloadedLibrary\Passive Components-Capacitors-Tantalum Capacitors.cml
C:\Users\Public\Documents\DesignSpark PCB\DownloadedLibrary\Passive Components-Fixed Resistors-Through Hole Fixed Resistors.cml
C:\Users\Public\Documents\DesignSpark PCB\DownloadedLibrary\Passive Components-Variable Resistors-Potentiometers.cml
C:\Users\Public\Documents\DesignSpark PCB\DownloadedLibrary\Passive Components-Variable Resistors-Trimmer Resistors.cml
C:\Users\Public\Documents\DesignSpark PCB\DownloadedLibrary\Power Connectors.cml
C:\Users\Public\Documents\DesignSpark PCB\DownloadedLibrary\Switching Diodes.cml

Selected items to be updated:
=============================

Components:
===========

    (None) 

Symbols:
========

    (None) 

Additional items to be updated:
===============================

Components:
===========

    (None) 

Symbols:
========

    (None) 

Selected items not to be updated  (Same version as library)
===========================================================

Components:
===========

508 10 pcb C:\Users\Public\Documents\DesignSpark PCB\DownloadedLibrary\DCDC convertors.cml

Symbols:
========

508 10pin Connector C:\Users\Public\Documents\DesignSpark PCB\DownloadedLibrary\Power Connectors.psl

Update Components Summary
=========================

Updating single component.
Update component values
Update component value positions
(Remove pad style exceptions on updated components)

	Selected for update:			   1  Component 
						   1  Symbol 

	Selected items to be updated:		   0  Components
						   0  Symbols

	Additional items to be updated:		   0  Components
						   0  Symbols

	Selected items NOT to be updated:	   1  Component 
	  (Same version as library)		   1  Symbol 

End Of Report.

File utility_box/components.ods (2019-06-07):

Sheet: Sheet1
description | manufacture | detail /mnfrn | supplier | quant | order code | price /pc | total | main properties
steel wall box |  |  | RS | 1 | 775-5338 | 50.5 | 50.5 | 210x600x400
din rail |  |  | RS | 2 | 467-406 | 4.7 | 9.4 | 500mm x 35mm x 7.5mm
relay brd |  |  | www.kiwi-electronics.n | 1 | WS-11638 | 22.95 | 22.95 | https://www.kiwi-electronics.nl/raspberry-pi-relais-board?lang=en
terminal jumpers |  | RS | RS | 5 | 878-7572 | 0.8
terminals |  | RS | RS | 10 | 878-7503 | 0.3 | 3
fuse |  |  | RS | 1 | 281-611 | 3.7 | 3.7
endbracket |  | RS | RS | 10 | 878-7553 | 0.45 | 4.5
5VDC DC | Mean Well | SD-25B-5 | RS | 1 | 183-887 | 28.63 | 28.63 | 25W 5V | 0 ~ 5A | 99*97*36mm (L*W*H)
12V DC DC | Mean Well | SD-25B-12 | RS | 1 | 183-871 | 28.63 | 28.63 | 25W 12V | 0-2,1A
ethernet switch |  |  | UA | 1 |  | 27 | 27
RJ 45 feed trought |  | CP30222SM3 | Farnell | 5 | 2366313 | 8.25 | 41.25 |  |  |  | alternatief | 2843017
mounting plate |  |  | UA | 1 |  | 50 | 50
24V connector |  |  | RS | 1 |  | 25 | 25
ethernet connextors |  |  |  | 3 |  | 3 | 9
raspberry pi |  |  | UA | 1 |  | 40 | 40
diode |  | BYW56 | Farnell | 2 | 1075758 | 0.51 | 1.03
cables |  | PP-6491B-1.50MMGRY |  |  | 2774317 |  | 20
 |  | PP-6491B-1.50MMBRN |  |  | 2774315
 |  | PP-6491B-1.50MMBLU |  |  | 2774314
 |  |  |  |  |  |  | 364.59
 |  |  |  |  |  | VAT | 76.56
 |  |  |  |  |  |  | 441.15
HV unit
DC DC |  | EMICO G10 | RS | 1 | 136-0451 | 113.77 | 113.77
cap HV |  | DEBF33D103ZB3B | RS | 5 | 721-5088 |  |  | 10n 2KV DC |  | niet meer leverbaar
cap LV |  | KRM55WR71H226MH01K | RS | 1 | 841-6731 | 4.36 | 4.36 | 22uF 50V
R 10M |  | HVC2512T1005JET |  | 1 | 2420580 | 4.85 | 4.85

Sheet: specs
specs | V | A
pump | 24 | 0.26
type | KNF | NMP830KNDC-B

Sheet: HV
switch | frequency | center | 125 | [kHz]
 |  | min | 60 | [kHz] | t | 16.67 | [us]
 | W |  | 376.99 | [krad/s]
nom voltage | 1000 | [V]
ripple | 0.1 | [%]
ripple | 1 | [V] | filter 1/k | tau = 1/(k*W) | 20 | 53.05 | [us] | 0 | [s]
ripple afterfilter | 0.05 | [V] | 50 | [mV]
 | C | 10 | [nF] | # | 5 | 50 | [nF] | 0 | F
 |  |  |  | R |  | 2 | [kohm] | 1061.03 | ohm
 |  |  |  | I load |  | 0.5 | [mA]
 |  |  |  | dV |  | 1 | [V]
In
I in max | 0.25 | [A] |  | Vnom | 890 | [V] |  | op voltage | 890 | [V]
 |  |  |  | I nom | 0.8 | [mA] |  | Vnom | 1000 | [V]
dVmax | 12 | [V] |  | Rnom calc | 1112.5 | [kohm] |  | max V in | 12 | [V]
 |  |  |  | Rnom fix | 1100 | [kohm] |  | nom Vin | 10.68
P[lost] | 3 | W
op V | 890 | [V]
I load | 0.81 | [mA] | Ifull load | 1.5 | [mA]
I in expected | 0.13 | [A]
dVmax | 13.32 | [V]
P[lost] | 1.8 | W | nominal
P[lost] | 1.82 | W | @ max volt
ADJ reg | Vin 15V
 |  | Vref | 1.25 | V | I adj | 0
 |  |  |  | Vout min | 6.36 | Voutmax | 10.97 |  | VhvMax | 914.35 | V
 |  | R1 | 270 |  |  |  |  |  | no load meas | 1000 | V
 |  | R2 fix | 1100 | R2 tot | 2100 |  |  |  | 1 M ohm | 932 | V
 |  | R3 pot | 1000
 |  |  |  | I min | 5 |  |  | Vout max reg
 |  |  |  | Rload max | 1.27 | kOhm |  | measured | 10.59
 |  |  |  | Rload | 1 | kOhm
 |  |  |  | Pload | 0.09 | [W]
 |  | power | Io = | 0.1 | [A]
 |  |  | Vin | 15 | V
 |  |  | Vout | 8 | V
 |  |  | P | 0.7 | W
 |  |  | Phi ja | 150 | C/W
 |  |  | dTj | 105 | C
 |  |  | Ta | 25 | C
 |  |  | Tj | 130

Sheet: 5Vpower
RaspPi | 2500
switch | 1000
Rn | 1000

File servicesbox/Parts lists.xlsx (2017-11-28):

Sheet: Cables
1 mtr power
 | qty | price each | Supplyer Order number | URL | Tot
4mm2 tri rated Black | 6 | £0.25 | A2TBK0040 | http://www.elandcables.com/cables/tri-rated-h05v2-k-h07v2-k-cable | £1.50
10 pos plug | 1 | £4.34 | 2509663 | http://uk.farnell.com/weidmuller/1944170000/terminal-block-pluggable-10pos/dp/2509663?MER=bn_level5_5NP_EngagementRec_1 | £4.34
10 pos plug | 1 | £5.27 | 2509651 | http://uk.farnell.com/weidmuller/1943660000/terminal-block-pluggable-10pos/dp/2509651?ost=1943660000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 | £5.27
Bias | 1 |  | 8719-LSF | http://www.elandcables.com/cables/belden-alternative-cable | £0.00
Braid | 1 | £7.77 | 1218647 | http://uk.farnell.com/te-connectivity-raychem/ray-101-6-0/sleeving-braid-6mm-silver-10m/dp/1218644?MER | £7.77
power line | 1 |  | A5G02040 | http://www.elandcables.com/electrical-cable-and-accessories/cables-by-type/rubber-flexible-cable
 |  |  |  |  | £18.88
 |  |  |  |  | £1132.80

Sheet: Servies Box
Description | MFG Part Number | Supplyer Part Number | Quantity | cost | Supplyer | Tot
Box | 20860-634 | 1816052 | 1 | 90 | http://uk.farnell.com/schroff/20860-634/rack-multipac-pro-4u-460-d-perfor/dp/1816052 | £90.00
clkplate | 20860-107 | 1370458 | 1 | 17 | http://uk.farnell.com/schroff/20860-107/chassis-plate-150d/dp/1370458?MER=bn_level5_5NP_EngagementRec_1 | £17.00
Powerplate | 20860-109 | 1370460 | 2 | 16 | http://uk.farnell.com/schroff/20860-109/chassis-plate-270d/dp/1370460?ost=20860-109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 | £32.00
Power inlet | 530763006 | 4884437 | 1 | 20.99 | http://uk.farnell.com/jaeger/530763006/plug-cable-socket-insert-4way/dp/4884437 | £20.99
Power Plug | 533763006 | 4884413 | 1 | 15 | http://uk.farnell.com/jaeger/533763006/receptacle-panel-pin-insert-4way/dp/4884413 | £15.00
Clamp | 630138006 | 4884050 | 1 | 5 | http://uk.farnell.com/jaeger/630-155-006/circular-clamp-industrial-series/dp/2395732 | £5.00
Bias Connection | MS3106E10SL-4S | 1339815 | 1 | 14.84 | http://uk.farnell.com/amphenol-industrial/ms3106e10sl-4s/connector-circular-2way/dp/1339815 | £14.84
Bias Plug | MS3102A-10SL4P | 634610 | 1 | 4.66 | http://uk.farnell.com/amphenol/ms3102a-10sl4p/plug-flange-2way/dp/634610 | £4.66
HDMI | NAHDMI-W | 1713531 | 1 | 11.02 | http://uk.farnell.com/neutrik/nahdmi-w/hdmi-1-3-feedthrough-adaptor/dp/1713531 | £11.02
ethernet | ECF504-SC5E | 1704447 | 1 | 4.33 | http://uk.farnell.com/l-com/ecf504-sc5e/adaptor-rj45-jack-rj45-jack-coupler/dp/1704447?MER=bn_level5_5NP_EngagementRec_4 | £4.33
Spacer | R30-3001002 | 517641 | 1 | 8.69 | http://uk.farnell.com/harwin/r30-3001002/spacer-m-f-10mm-pk25/dp/517641 | £8.69
Spring | D01133 | 1624024 | 1 | 0.74 | http://uk.farnell.com/duratool/d01133/washer-steel-bzp-m3-pk100/dp/1624024 | £0.74
M3 screw | M36 PRSTMCZ100- | 1419986 | 1 | 1.66 | http://uk.farnell.com/duratool/m36-prstmcz100/screw-steel-bzp-6mm-m3-pk100/dp/1419986?MER=bn_search_1TP_SearchNB_1 | £1.66
M3 Nut | M3- HFST-Z100- | 1419447 | 1 | 1.33 | http://uk.farnell.com/duratool/m3-hfst-z100/nut-full-steel-bzp-m3-pk100/dp/1419447?MER=bn_search_1TP_SearchNB_1 | £1.33
cable socket | 042 953 006 | 2395726 | 1 | 11.36 | http://uk.farnell.com/jaeger/042-953-006/connector-circular-plug-3pos-cable/dp/2395726 | £11.36
chassis | 038 351 006 | 2395727 | 1 | 5.68 | http://uk.farnell.com/jaeger/038-351-006/connector-circular-rcpt-3pos-panel/dp/2395727 | £5.68
clamp | 630135006 | 4883573 | 1 | 5.9 | http://uk.farnell.com/jaeger/630135006/cable-clamp-size-1/dp/4883573?ost=630135006 | £5.90
5V dc dc convertor | SD-25C-5 | 678-3568 | 1 | £27.00 | http://uk.rs-online.com/web/p/isolated-dc-dc-converters/6783568/ | £27.00
12 volt dcdc convertor | SD-25C-12 | 183-865 | 1 | £27.00 | http://uk.rs-online.com/web/p/isolated-dc-dc-converters/0183865/ | £27.00
din rail | SZ2314000 | 283-5690 | 1 | £2.74 | http://uk.rs-online.com/web/p/din-rails/2835690/ | £2.74
terminal |  | 815-666 | 4 | £0.44 | http://uk.rs-online.com/web/p/products/0815694/ | £1.76
Plate |  | 872-4726 | 3 | £0.15 | http://uk.rs-online.com/web/p/din-rail-terminal-accessories/0501746/?origin=PSF_435779|acc | £0.45
Bookend |  | 652-3672 | 5 | £0.25 | http://uk.rs-online.com/web/p/din-rail-terminal-accessories/6523672/ | £1.25
earth |  | 872-5628 | 1 | £1.97 | http://uk.rs-online.com/web/p/earth-blocks/0501815/ | £1.97
pole jumper |  | 815-795 | 5 | £2.01 | http://uk.rs-online.com/web/p/products/0815795/ | £2.11
Fan | 3412NLE | 773-4429 | 1 | £17.74 | http://uk.rs-online.com/web/p/axial-fans/7734429/ | £2.11

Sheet: DCDC fanout
Boards | dc fanout
10
 | Description | MFG Part Number | Supplyer Part Number | Quantity Per Unit | cost Each | Supplyer | Tot
 | Line filer | BNX002-01 | 9526960 | 30 | 7.82 | http://uk.farnell.com/murata/bnx005-01/filter-dc-power-15a/dp/9526960 | £234.60
 | Line filer | BNX005-01 | 9526943 | 3 | 4.13 | http://uk.farnell.com/murata/bnx002-01/filter-power-emi-10a/dp/9526943?MER=bn_level5_4NP_CtbtGlobal_1 | £12.39
 | Cerm cap | RPER71H104K2S1A03A | 6530181 | 3 | 0.5 | http://uk.rs-online.com/web/p/ceramic-multilayer-capacitors/6530181/ | £1.50
 | Tant cap | TR3E106M050C0300 | 6845307 | 14 | 1.25 | http://uk.rs-online.com/web/p/tantalum-capacitors/6845307/ | £17.50
 | Connectors | 282836-8 | 3617730 | 2 | 1.17 | http://uk.rs-online.com/web/p/pcb-terminal-blocks/3617730/ | £2.34
 | Power coupling plug | BL 5.08/4 | 1131814 | 1 | 1.4 | http://uk.farnell.com/weidmuller/bl-5-08-4/terminal-block-pluggable-4pos/dp/1131814?ost=BL+5.08%2F4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 | £1.40
 | Power coupling socket | BL 5.08/4 | 2509517 | 1 | 0.66 | http://uk.farnell.com/weidmuller/1149440000/terminal-block-header-4pos-th/dp/2509517 | £0.66
 | power socket | SL 5.08HC/10/180LF 1148150000 | 2509512 | 10 | 1.43 | http://uk.farnell.com/weidmuller/1148150000/terminal-block-header-10pos-th/dp/2509512?ost=1148150000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 | £14.30
 | 48 to 5 | IFH20048S05 | IFH20048S05 | 1 | 148 | XP Power | £148.00
 | 48 to 3.3 | ICH5048WS3V3 | ICH5048WS3V3 | 1 | 52.5 | XP Power | £52.50
 | 48 to 5 | ICH5048WS05 | ICH5048WS05 | 1 | 70 | XP Power | £70.00
 | Heat sink ICH | Heat sink ICH |  | 2 | 5 | XP Power | £10.00
 | Heatsink IFH | Heatsink IFH |  | 1 | 5 | XP Power | £5.00

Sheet: Patch Pannel
Description | MFG Part Number | Supplyer Part Number | Quantity | cost | Supplyer
48Vsocket cable | 530763006 | 4884437 | 6 | 20.99 | http://uk.farnell.com/jaeger/530763006/plug-cable-socket-insert-4way/dp/4884437
48v Plug pannel | 533763006 | 4884413 | 6 | 15 | http://uk.farnell.com/jaeger/533763006/receptacle-panel-pin-insert-4way/dp/4884413
Clamp | 630138006 | 4884050 |  | 5 | http://uk.farnell.com/jaeger/630-155-006/circular-clamp-industrial-series/dp/2395732

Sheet: 5 volt and bias power
Description | MFG Part Number | Supplyer Part Number | Quantity | cost | Supplyer | Tot
5V dc dc convertor | SD-25C-5 | 678-3568 | 1 | £27.00 | http://uk.rs-online.com/web/p/isolated-dc-dc-converters/6783568/ | £27.00
12 volt dcdc convertor | SD-25C-12 | 183-865 | 1 | £27.00 | http://uk.rs-online.com/web/p/isolated-dc-dc-converters/0183865/ | £27.00
din rail | SZ2314000 | 283-5690 | 1 | £2.74 | http://uk.rs-online.com/web/p/din-rails/2835690/ | £2.74
terminal |  | 815-666 | 4 | £0.44 | http://uk.rs-online.com/web/p/products/0815694/ | £1.76
Plate |  | 872-4726 | 3 | £0.15 | http://uk.rs-online.com/web/p/din-rail-terminal-accessories/0501746/?origin=PSF_435779|acc | £0.45
Bookend |  | 652-3672 | 5 | £0.25 | http://uk.rs-online.com/web/p/din-rail-terminal-accessories/6523672/ | £1.25
earth |  | 872-5628 | 1 | £1.97 | http://uk.rs-online.com/web/p/earth-blocks/0501815/ | £1.97
pole jumper |  | 815-795 | 5 | £2.01 | http://uk.rs-online.com/web/p/products/0815795/ | £2.11
Fan | 3412NLE | 773-4429 | 1 | £17.74 | http://uk.rs-online.com/web/p/axial-fans/7734429/ | £2.11
 |  |  |  |  |  | £64.28

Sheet: Powerbox
Description | MFG Part Number | Stock number | Supplyer Part Number | Quantity | cost | Supplyer | Tot
Power connector | 533760006 |  | http://uk.farnell.com/jaeger/533760006/receptacle-panel-skt-insert-4way/dp/4884450 | 6 | 24.7 | farnell
Circuit breaker |  |  | http://uk.farnell.com/abb/ds201mb16a30/circuit-breaker-rcbo-230vac-16a/dp/2506889
Relay |  | 178-2220 | http://uk.rs-online.com/web/p/non-latching-relays/1782220/ | 1
Contacts |  | 290-1315 | http://uk.rs-online.com/web/p/pcb-terminal-blocks/2901315/ | 3
1.2 k 0603 resistor |  | 820-6770 | http://uk.rs-online.com/web/p/surface-mount-fixed-resistors/8206770/ | 2
PCB Header |  | 532-030 | http://uk.rs-online.com/web/p/pcb-headers/0532030/ | 3
 |  | 532-399 | http://uk.rs-online.com/web/p/pcb-connector-housings/0532399/?origin=PSF_435697|acc | 3
 |  | 532-456 | http://uk.rs-online.com/web/p/pcb-connector-contacts/0532456/?origin=PSF_435696|acc | 40
Inhibit LED res |  | 213-2266 | http://uk.rs-online.com/web/p/surface-mount-fixed-resistors/2132266/ | 6
Inhibit LED |  | 228-6004 | http://uk.rs-online.com/web/p/visible-leds/2286004/?origin=PSF_438287|acc | 6
LED Bezzel |  | 262-2999 | http://uk.rs-online.com/web/p/led-bezels/2622999/?origin=PSF_438264|acc | 12
DC FAIL LED |  | 228-6004 | http://uk.rs-online.com/web/p/visible-leds/2286004/?origin=PSF_438287|acc
 |  |  | http://uk.rs-online.com/web/p/bipolar-transistors/4452051/?source=DS
 |  |  | http://uk.rs-online.com/web/p/led-bezels/2622999/
 |  | 178-2220 | 2
 | x | 290-1315 | 10
 |  | 532-030 | 10
 |  | 532-399 | 10
 |  | 532-456 | 100
 |  | 228-6004 | 15
 |  | 228-5988 | 15
 |  | 262-2999 | 30
 |  | 445-2051 | 50
 |  | 679-0541 | 50
 |  | 213-2367 | 50
 |  | 678-9888 | 50
 |  | 734-7154 | 20
 |  | 850-8603 | 3
 |  | 324-6401 | 9
 | x | 708-7613 | 20
 |  | 377-9759 | 3
 |  | 706-6192 | 2
 |  | 487-832 | 1
 | Interlock con | MS3102A-10SL-3S

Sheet: Sheet1
 |  | Service box | 48 Cable | 24 Cable | 24 Power Supply | 48 Power Supply | 48 service supply | Patch Panel
 | L Cable mount Plug |  | 6
 | L Chasses Mount Plug | 6 |  |  |  |  |  | 12
 | L Cable mount Socket |  | 6
 | L Chasses Mount Socket |  |  |  | 6 | 6
 | S Cable mount Plug |  |  | 6
 | S Chasses Mount Plug | 6 |  |  |  |  |  | 10
 | S Cable mount Socket |  |  | 6 |  |  |  | 10
 | S Chasses Mount Socket |  |  |  |  |  | 6
 |  | Need | Got | then buy | RS number |  | clamp
1 | Large chasis Mount socket Rapid | 12 | 9 | 3 | 324-6401 | 533 760 006
2 | Large cable mount plug rapid | 12 | 8 | 4 |  | 530 754 006 | 4884050
3 | large cable mount socket | 24 | 16 | 8 |  | 530 763 006 | 4884050
4 | large chasis mount plug | 24 | 15 | 9 |  | 533 763 006
5 | Small chasis Mount socket | 6 | 0 | 6 |  | 536 603 006
6 | Small cable mount plug | 6 | 0 | 6 |  | 532 603 006
7 | Small cable mount socket | 16 | 2 | 14 |  | 042 953 006
8 | Small chasis mount plug | 16 | 1 | 15 | 2395727 | 038 351 006

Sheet: Sheet2
Description | MFG Part Number | Supplyer Part Number | Quantity Per Unit | Units | Quantity Total | cost Each | Supplyer | Tot per box
PCB | none | none | 1 | 6 | 6 | 279 |  | £279.00
Line filer | BNX002-01 | 9526960 | 30 | 6 | 180 | 7.82 | http://uk.farnell.com/murata/bnx005-01/filter-dc-power-15a/dp/9526960 | £234.60
Line filer | BNX005-01 | 9526943 | 3 | 6 | 18 | 4.13 | http://uk.farnell.com/murata/bnx002-01/filter-power-emi-10a/dp/9526943?MER=bn_level5_4NP_CtbtGlobal_1 | £12.39
Cerm cap | RPER71H104K2S1A03A | 6530181 | 2 | 6 | 12 | 0.5 | http://uk.rs-online.com/web/p/ceramic-multilayer-capacitors/6530181/ | £1.00
Tant cap | TR3E106M050C0300 | 6845307 | 14 | 6 | 84 | 1.25 | http://uk.rs-online.com/web/p/tantalum-capacitors/6845307/ | £17.50
Connectors | 282836-8 | 3617730 | 2 | 6 | 12 | 1.17 | http://uk.rs-online.com/web/p/pcb-terminal-blocks/3617730/ | £2.34
Power coupling plug | BL 5.08/4 | 1131814 | 10 | 6 | 60 | 1.4 | http://uk.farnell.com/weidmuller/bl-5-08-4/terminal-block-pluggable-4pos/dp/1131814?ost=BL+5.08%2F4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 | £14.00
Power coupling socket | BL 5.08/4 | 2509517 | 10 | 6 | 60 | 0.66 | http://uk.farnell.com/weidmuller/1149440000/terminal-block-header-4pos-th/dp/2509517 | £6.60
power socket | SL 5.08HC/10/180LF 1148150000 | 2509512 | 10 | 6 | 60 | 1.43 | http://uk.farnell.com/weidmuller/1148150000/terminal-block-header-10pos-th/dp/2509512?ost=1148150000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 | £14.30
48 to 5 | IFH20048S05 | IFH20048S05 | 1 | 6 | 148 | £148.00 | XP Power | £148.00
48 to 3.3 | ICH5048WS3V3 | ICH5048WS3V3 | 1 | 6 | 52.5 | £52.50 | XP Power | £52.50
48 to 5 | ICH5048WS05 | ICH5048WS05 | 1 | 6 | 70 | £70.00 | XP Power | £70.00
Heat sink ICH | Heat sink ICH |  | 2 | 6 | 5 | £10.00 | XP Power | £20.00
Heatsink IFH | Heatsink IFH |  | 1 | 6 | 5 | £5.00 | XP Power | £5.00
Box | 20860-634 | 1816052 | 1 | 6 | 6 | 90 | http://uk.farnell.com/schroff/20860-634/rack-multipac-pro-4u-460-d-perfor/dp/1816052 | £90.00
clkplate | 20860-107 | 1370458 | 1 | 6 | 6 | 17 | http://uk.farnell.com/schroff/20860-107/chassis-plate-150d/dp/1370458?MER=bn_level5_5NP_EngagementRec_1 | £17.00
Powerplate | 20860-109 | 1370460 | 2 | 6 | 12 | 16 | http://uk.farnell.com/schroff/20860-109/chassis-plate-270d/dp/1370460?ost=20860-109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 | £32.00
Power inlet | 530763006 | 4884437 | 1 | 6 | 6 | 20.99 | http://uk.farnell.com/jaeger/530763006/plug-cable-socket-insert-4way/dp/4884437 | £20.99
Power Plug | 533763006 | 4884413 | 1 | 6 | 6 | 15 | http://uk.farnell.com/jaeger/533763006/receptacle-panel-pin-insert-4way/dp/4884413 | £15.00
Clamp | 630138006 | 4884050 | 1 | 6 | 6 | 5 | http://uk.farnell.com/jaeger/630-155-006/circular-clamp-industrial-series/dp/2395732 | £5.00
Bias Connection | MS3106E10SL-4S | 1339815 | 1 | 6 | 6 | 14.84 | http://uk.farnell.com/amphenol-industrial/ms3106e10sl-4s/connector-circular-2way/dp/1339815 | £14.84
Bias Plug | MS3102A-10SL4P | 634610 | 1 | 6 | 6 | 4.66 | http://uk.farnell.com/amphenol/ms3102a-10sl4p/plug-flange-2way/dp/634610 | £4.66
HDMI | NAHDMI-W | 1713531 | 2 | 6 | 12 | 11.02 | http://uk.farnell.com/neutrik/nahdmi-w/hdmi-1-3-feedthrough-adaptor/dp/1713531 | £22.04
ethernet | ECF504-SC5E | 1704447 | 1 | 6 | 6 | 4.33 | http://uk.farnell.com/l-com/ecf504-sc5e/adaptor-rj45-jack-rj45-jack-coupler/dp/1704447?MER=bn_level5_5NP_EngagementRec_4 | £4.33
Spacer | R30-3001002 | 517641 | 1 | 6 | 6 | 8.69 | http://uk.farnell.com/harwin/r30-3001002/spacer-m-f-10mm-pk25/dp/517641 | £8.69
Spring | D01133 | 1624024 | 1 | 6 | 6 | 0.74 | http://uk.farnell.com/duratool/d01133/washer-steel-bzp-m3-pk100/dp/1624024 | £0.74
M3 screw | M36 PRSTMCZ100- | 1419986 | 1 | 6 | 6 | 1.66 | http://uk.farnell.com/duratool/m36-prstmcz100/screw-steel-bzp-6mm-m3-pk100/dp/1419986?MER=bn_search_1TP_SearchNB_1 | £1.66
M3 Nut | M3- HFST-Z100- | 1419447 | 1 | 6 | 6 | 1.33 | http://uk.farnell.com/duratool/m3-hfst-z100/nut-full-steel-bzp-m3-pk100/dp/1419447?MER=bn_search_1TP_SearchNB_1 | £1.33
cable socket | 042 953 006 | 2395726 | 1 | 6 | 6 | 11.36 | http://uk.farnell.com/jaeger/042-953-006/connector-circular-plug-3pos-cable/dp/2395726 | £11.36
chassis | 038 351 006 | 2395727 | 1 | 6 | 6 | 5.68 | http://uk.farnell.com/jaeger/038-351-006/connector-circular-rcpt-3pos-panel/dp/2395727 | £5.68
clamp | 630135006 | 4883573 | 1 | 6 | 6 | 5.9 | http://uk.farnell.com/jaeger/630135006/cable-clamp-size-1/dp/4883573?ost=630135006 | £5.90
5V dc dc convertor | SD-25C-5 | 678-3568 | 1 | 6 | 6 | £27.00 | http://uk.rs-online.com/web/p/isolated-dc-dc-converters/6783568/ | £27.00
12 volt dcdc convertor | SD-25C-12 | 183-865 | 1 | 6 | 6 | £27.00 | http://uk.rs-online.com/web/p/isolated-dc-dc-converters/0183865/ | £27.00
din rail | SZ2314000 | 283-5690 | 1 | 6 | 6 | £2.74 | http://uk.rs-online.com/web/p/din-rails/2835690/ | £2.74
terminal |  | 815-666 | 4 | 6 | 24 | £0.44 | http://uk.rs-online.com/web/p/products/0815694/ | £1.76
Plate |  | 872-4726 | 3 | 6 | 18 | £0.15 | http://uk.rs-online.com/web/p/din-rail-terminal-accessories/0501746/?origin=PSF_435779|acc | £0.45
Bookend |  | 652-3672 | 5 | 6 | 30 | £0.25 | http://uk.rs-online.com/web/p/din-rail-terminal-accessories/6523672/ | £1.25
earth |  | 872-5628 | 1 | 6 | 6 | £1.97 | http://uk.rs-online.com/web/p/earth-blocks/0501815/ | £1.97
pole jumper |  | 815-795 | 5 | 6 | 30 | £2.01 | http://uk.rs-online.com/web/p/products/0815795/ | £10.05
Fan | 3412NLE | 773-4429 | 1 | 6 | 6 | £17.74 | http://uk.rs-online.com/web/p/axial-fans/7734429/ | £17.74
 |  |  |  |  |  |  |  | £1228.41 | £7370.46

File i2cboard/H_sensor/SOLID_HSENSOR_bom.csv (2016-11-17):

SOLID Humidity sensor::Version 1.0::::::
Resistors 1%  in not indicated otherwise::::::::
Capicitors  10V  / 20 %  if not indicated otherwise::::::::
::::::::
Part:Value:Device:Package:Description:MPN:OC_FARNELL:PARTNO:SUPPLIER
C5:100n:C-EUC0805:C0805:CAPACITOR, European symbol:::*:
R1:0R:R-EU_R0402:R0402:RESISTOR, European symbol::::
R13:10K:R-EU_R0402:R0402:RESISTOR, European symbol::::
U1:NC:NCP170:SOT563::NCP170AXV330T2G:2507604::ON
U8:HTS221:HTS221:HLGA-6:Capacitive humidity sensor:HTS221:2433085::ST
X1:MICROMATCH-6SMD:MICROMATCH-6SMD:MICROMATCH_SMD-6:MicroMaTch 6  7-215464-6 / 0-215464-6:7-188275-6:1056234::

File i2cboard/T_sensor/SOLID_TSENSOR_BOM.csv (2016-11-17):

SOLID Temperature sensor |  | V 2.0
Resistors 1% in not indicated otherwise
Capicitors 10V / 20 % if not indicated otherwise
value NC means do not place
Qty | Value | Device | Package | Parts | Description | MPN | OC_FARNELL | OC_NEWARK | PACKAGE | PARTNO | SUPPLIER | TP_SIGNAL_NAME
1 | 0R | R-EU_R0402 | R0402 | R1 | RESISTOR, European symbol
1 | 100n | C-EUC0805 | C0805 | C5 | CAPACITOR, European symbol |  |  |  |  | *
4 | 10K | R-EU_R0402 | R0402 | R3, R4, R5, R13 | RESISTOR, European symbol
3 | 1K | R-EU_R0402 | R0402 | R6, R10, R11 | RESISTOR, European symbol
1 | AT30TSE752-XM8-B | AT30TSE752-XM8-B | SOP65P490X110-8N | U20 | SENSOR, TEMP, 9-12BIT, 2KB EEPROM, MSOP-8 | AT30TSE752-XM8-B | 2115206 | Unknown | MSOP-8 |  | ATMEL
1 | MICROMATCH-6SMD | MICROMATCH-6SMD | MICROMATCH_SMD-6 | X1 | MicroMaTch 6 7-215464-6 / 0-215464-6 | 7-188275-6 | 1056234
1 | NC | NCP170 | SOT563 | U1 |  | NCP170AXV330T2G | 2507604 |  |  |  | ON
2 | NC | UA_TPPAD1-13 | UA_P1-13 | T0, T1 | Test pad |  |  |  |  | *

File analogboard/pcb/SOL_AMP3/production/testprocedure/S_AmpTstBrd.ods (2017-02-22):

 |  | Qty | Value | Device | Package | Parts | Description | BOM | DNP | MF | MPN | OC_FARNELL | OC_NEWARK | PACKAGE | PARTNO | SUPPLIER | TOL | TP_SIGNAL_NAME | VOLT
1300 | 1300 | 1 |  | FRDM-KL25ZARDUINO | FRDM-KL25Z | FRDM1 | For creating FRDM-KL25Z shields |  |  |  |  |  |  |  | FRDM-KL25Z
1 | 1 | 1 | 0R | R-EU_R0805 | R0805 | R26 | RESISTOR, European symbol
2 | 1 | 2 | 0R | R_HAND | R0805H | R1, R19 |  |  |  |  |  |  |  |  |  |  | 0.1
104 | 2 | 52 | 100n | C-EUC0805K | C0805K | C1, C2, C3, C4, C5, C6, C7, C8, C9, C10, C11, C12, C13, C14, C15, C18, C19, C20, C22, C23, C24, C25, C26, C27, C28, C29, C30, C32, C35, C36, C37, C38, C39, C40, C41, C42, C48, C49, C54, C57, C58, C60, C61, C62, C63, C64, C65, C67, C68, C69, C70, C72 | CAPACITOR, European symbol
20 | 1 | 20 | 10K | R-EU_R0805 | R0805 | R3, R6, R7, R8, R9, R10, R11, R12, R13, R28, R29, R30, R32, R34, R35, R36, R37, R51, R54, R55 | RESISTOR, European symbol
2 | 2 | 1 | 10p | C-EUC0805K | C0805K | C71 | CAPACITOR, European symbol
30 | 10 | 3 | 10u | CPOL-EUSMCA | SMC_A | C17, C21, C45 | POLARIZED CAPACITOR, European symbol
1 | 1 | 1 | 12K | R-EU_R0805 | R0805 | R52 | RESISTOR, European symbol
8 | 2 | 4 | 15p | C-EUC0805K | C0805K | C33, C43, C50, C52 | CAPACITOR, European symbol
1 | 1 | 1 | 18K | R-EU_R0805 | R0805 | R53 | RESISTOR, European symbol
20 | 20 | 1 | 1A F | FUSE | FUSE1206 | F3 |  |  |  |  | 3413.0115.22 | 7785739 |  |  |  | SCHURTER
2 | 1 | 2 | 1K | R_HAND | R0805H | R4, R20
24 | 2 | 12 | 1R | R-EU_R1206 | R1206 | R38, R39, R40, R41, R42, R44, R45, R46, R47, R48, R49, R50 | RESISTOR, European symbol
20 | 20 | 1 | 2.0A F | FUSE | FUSE1206 | F2 |  |  |  |  | 3413.0119.22 | 7785763 |  |  |  | SCHURTER
100 | 50 | 2 | 22-23-2021 | 22-23-2021 | 22-23-2021 | X3, X6 | .100 (2.54mm) Center Header - 2 Pin |  |  | MOLEX | 22-23-2021 | 1462926 | 25C3832
100 | 50 | 2 | 22-23-2031 | 22-23-2031 | 22-23-2031 | X5, X8 | .100 (2.54mm) Center Header - 3 Pin |  |  | MOLEX | 22-23-2031 | 1462950 | 30C0862
150 | 50 | 3 | 22-23-2041 | 22-23-2041 | 22-23-2041 | X2, X4, X7 | .100 (2.54mm) Center Header - 4 Pin |  |  | MOLEX | 22-23-2041 | 1462920 | 38C0355
2 | 1 | 2 | 24.3 | R_HAND | R0805H | R17, R31 |  |  |  |  |  |  |  |  |  |  | 0.1
1 | 1 | 1 | 27K | R-EU_R0805 | R0805 | R2 | RESISTOR, European symbol
70 | 35 | 2 | 3.3uH | LQH44P | LQH44P | L1, L2 | MuRata ChipCoils LQH44P series |  |  |  | LQH44PN3R3MP0 | 1782797
1 | 1 | 1 | 3K | R-EU_R0805 | R0805 | R56 | RESISTOR, European symbol
18 | 2 | 9 | 4.7n | C-EUC0805K | C0805K | C31, C34, C44, C46, C51, C53, C55, C56, C59 | CAPACITOR, European symbol |  |  | TDK
4 | 2 | 2 | 4K2 | R_HAND | R0805H | R5, R21
8 | 2 | 4 | 4K3 | R_HAND | R0805H | R16, R18, R33, R43 |  |  |  |  |  |  |  |  |  |  | 0.1
6 | 2 | 3 | 4K7 | R-EU_R0805 | R0805 | R14, R15, R57 | RESISTOR, European symbol
750 | 150 | 5 | 5V_500mA | REEDRELAY | REED | K1, K2, K3, K5, K6 | RELAY |  |  | 05/01/07 | COTO TECHNOLOGY | 1081622 | unknown
4 | 1 | 4 | ?K | R-EU_R0805 | R0805 | R22, R23, R24, R25 | RESISTOR, European symbol
800 | 400 | 2 | AD8132ARZ | AD8132ARZ | SOIC127P600X175-8N | U1, U4 | Low Cost, High Speed Differential Amplifier |  |  | Analog Devices |  | 9426043 | 19M8885 | SOIC-8 | AD8132ARZ
1500 | 750 | 2 | ADG1608BRUZ | ADG1608BRUZ | SOP65P640X120-16N | U2, U3 | 4.5 RON, 4-/8-Channel 5 V,+12 V, +5 V, and +3.3 V Multiplexers |  |  |  | ADG1608BRUZ | 1827330 | 26R2416 | TSSOP-16 |  | Analog Devices
600 | 300 | 2 | ADG734BRUZ | ADG734BRUZ | SOP65P640X120-20N | U5, U6 | CMOS, 2.5Low Voltage, Triple/Quad SPDT Switches |  |  |  | ADG734BRUZ | 1661037 | 59K1572 | TSSOP-20 |  | Analog devices
1.5 | 0.15 | 10 | BSS138 | NFET | SOT23 | Q1, Q2, Q3, Q4, Q5, Q6, Q7, Q8, Q9, Q10 |  |  |  |  |  |  |  |  | FET
400 | 400 | 1 | FAB64 | FAB64 | FAB64 | X1 | CONNECTOR
270 | 270 | 1 | INA193 | INA193 | SOT23-5 | U8 | Current Sense Amplifier, Common-Mode Range |  |  |  | INA193AQDBVRQ1 | 1903412
10 | 10 | 1 | JUMPER-3PTH | JUMPER-3PTH | 1X03 | JP1
135 | 135 | 1 | LP38692MP-ADJ | LP38692MP-ADJ | SOT150P696X180-5N | U22 | Linear Regulator |  |  |  | LP38692MP-ADJ | 1008058 | 41K7473 | SOT-223-5 |  | NationalSemiconductor
400 | 400 | 1 | LT3015EMSEM | LT3015EMSEM | SOP65P490X110H-13N | U14 | Linear Regulator
0 |  | 1 | NC | R-EU_R0402 | R0402 | R27 | RESISTOR, European symbol |  |  |  |  |  |  |  | *
0 |  | 9 | UA_TPPAD1-13 | UA_TPPAD1-13 | UA_P1-13 | T2, T4, T5D, T6, T7, TG4, TG5, TM5, TVN3 | Test pad |  |  |  |  |  |  |  | *
70 | 70 | 1 | ZXCT1109SA-7 | ZXCT1109SA-7 | SOT91P240X110-3N | U7 | LOW POWER HIGH-SIDE CURRENT MONITORS |  |  |  | ZXCT1109SA-7 | 1904028 | 55T4048 | SOT-23-3 |  | DIODES INC.
0 |  | 3 | nc | CPOL-EUSMCA | SMC_A | C16, C47, C66 | POLARIZED CAPACITOR, European symbol
6935.5
80 | 10 | 800
303
500
 |  |  | 6.3 | 161.28
 |  |  | 3.9 | 99.84

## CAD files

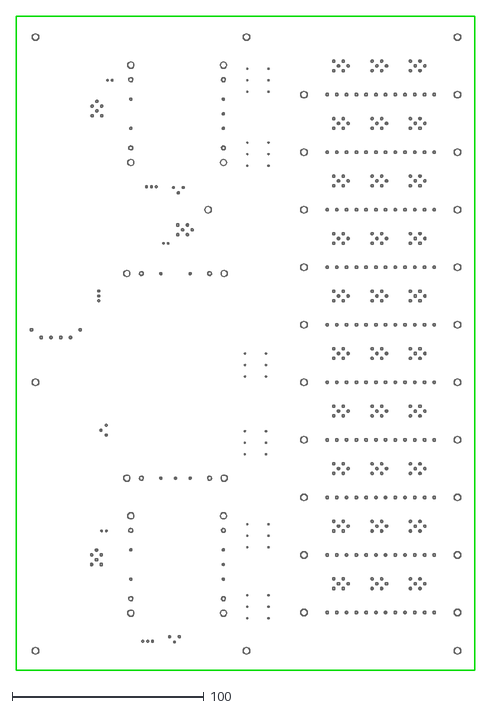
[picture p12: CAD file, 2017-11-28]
servicesbox/solid_services_box_main_power_pcb/Solid power fan-out.dxf
239.0 x 341.0

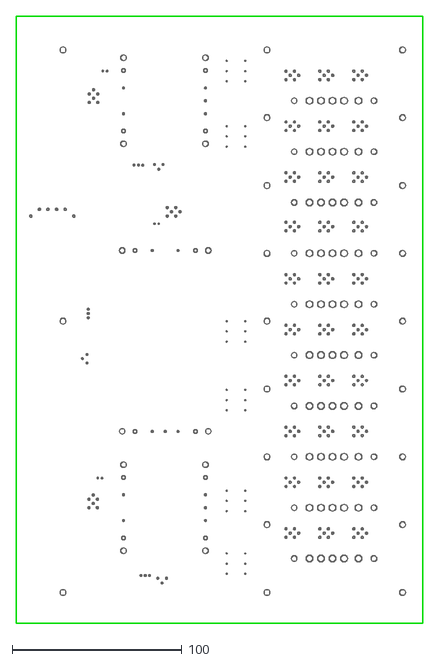
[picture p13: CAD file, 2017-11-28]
servicesbox/solid_services_box_main_power_pcb/Solid power fan-outBAK.dxf
240.0 x 358.0

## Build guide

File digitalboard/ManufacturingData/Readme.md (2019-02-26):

Manufacturing Data for ADC+FPGA Readout Board
=============================================

_Data for PCB fabrication, list of components ( BoM ) , component assembly information._

N.B. This is a copy of information at https://svn2.phy.bris.ac.uk/svn/uob-hep-pc051a

Contains information for :

1) main board
* pc051c-manufacturing-artwork-2017-04-25.zip
2) I2C pass-through ( that connects I2C busses to sensors in frame )
* pc051c_i2c_passthrough.pdf (Circuit schematic)
* pc051c_i2c_passthrough-manufacturing-artwork-2017-04-28.zip ( Gerber files, drill, ODB++, bill of materials )
* pc051c_i2c_passthrough_04_assembly.pdf ( Assembly drawing )
3) Power filter / distribution board
* pc051c_power_filter-manufacturing-artwork-2017-05-05.zip ( Gerber files, drill, ODB++, bill of materials  )
* pc051c_power_filter.pdf (Circuit schematic)

Changes made on the ADC board 

19 October 2017 

all boards for module 1 .. 4 

Put in parallel to R19   a resistor of 180K 

modified boards see 

https://docs.google.com/spreadsheets/d/17iVyDD3zpS0zKJI71sC7qOBFLLtJkKOROC2uzFVCJ_E/edit?usp=sharing_eip&ts=5a1d8e48

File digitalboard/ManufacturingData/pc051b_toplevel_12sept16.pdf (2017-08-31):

## POWER REGULATION

## 8 X LTM9007

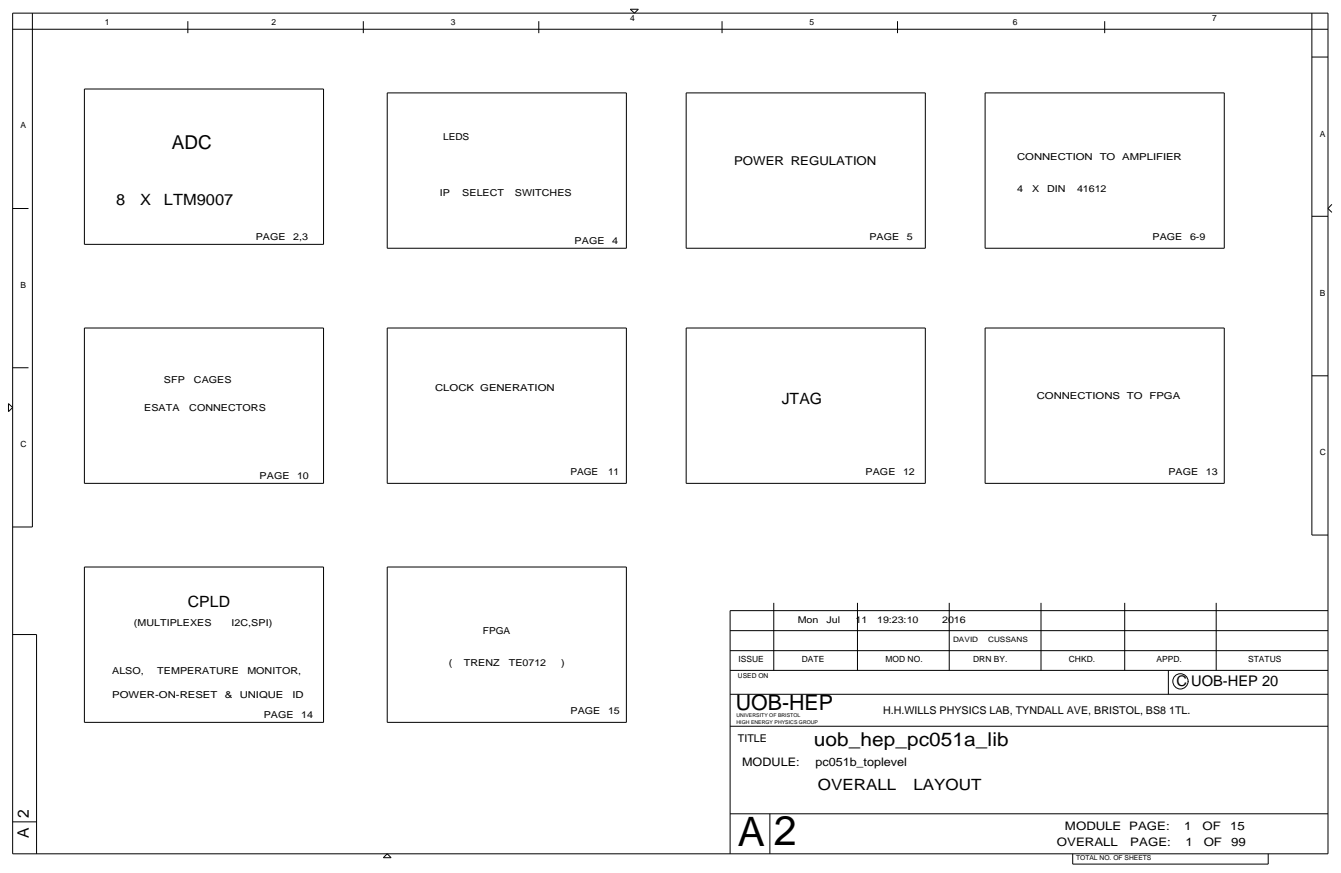
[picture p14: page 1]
PAGE 15; FPGA; ( TRENZ TE0712; PAGE 14; PAGE 13; JTAG; PAGE 12 PAGE 10; SFP CAGES; 4 X DIN 41612; PAGE 5; PAGE 6-9 PAGE 4 PAGE 2,3; LEDS ADC; OVERALL LAYOUT; PAGE 11; CLOCK GENERATION; ESATA CONNECTORS; CPLD; (MULTIPLEXES; I2C,SPI); ALSO,; TEMPERATURE MONITOR,; uob_hep_pc051a_lib; UOB-HEP

CONNECTION TO AMPLIFIER

IP SELECT SWITCHES

CONNECTIONS TO FPGA

Mon Jul | 11 19:23:10 2016

DAVID CUSSANS

ISSUE | DATE | MOD NO. | DRN BY. | CHKD. | APPD. | STATUS

USED ON | C UOB-HEP 20

POWER-ON-RESET & UNIQUE ID

H.H.WILLS PHYSICS LAB, TYNDALL AVE, BRISTOL, BS8 1TL.

UNIVERSITY OF BRISTOL
HIGH ENERGY PHYSICS GROUP
TITLE
MODULE: pc051b_toplevel

MODULE PAGE: 1 OF 15
OVERALL PAGE: 1 OF 99

TOTAL NO. OF SHEETS

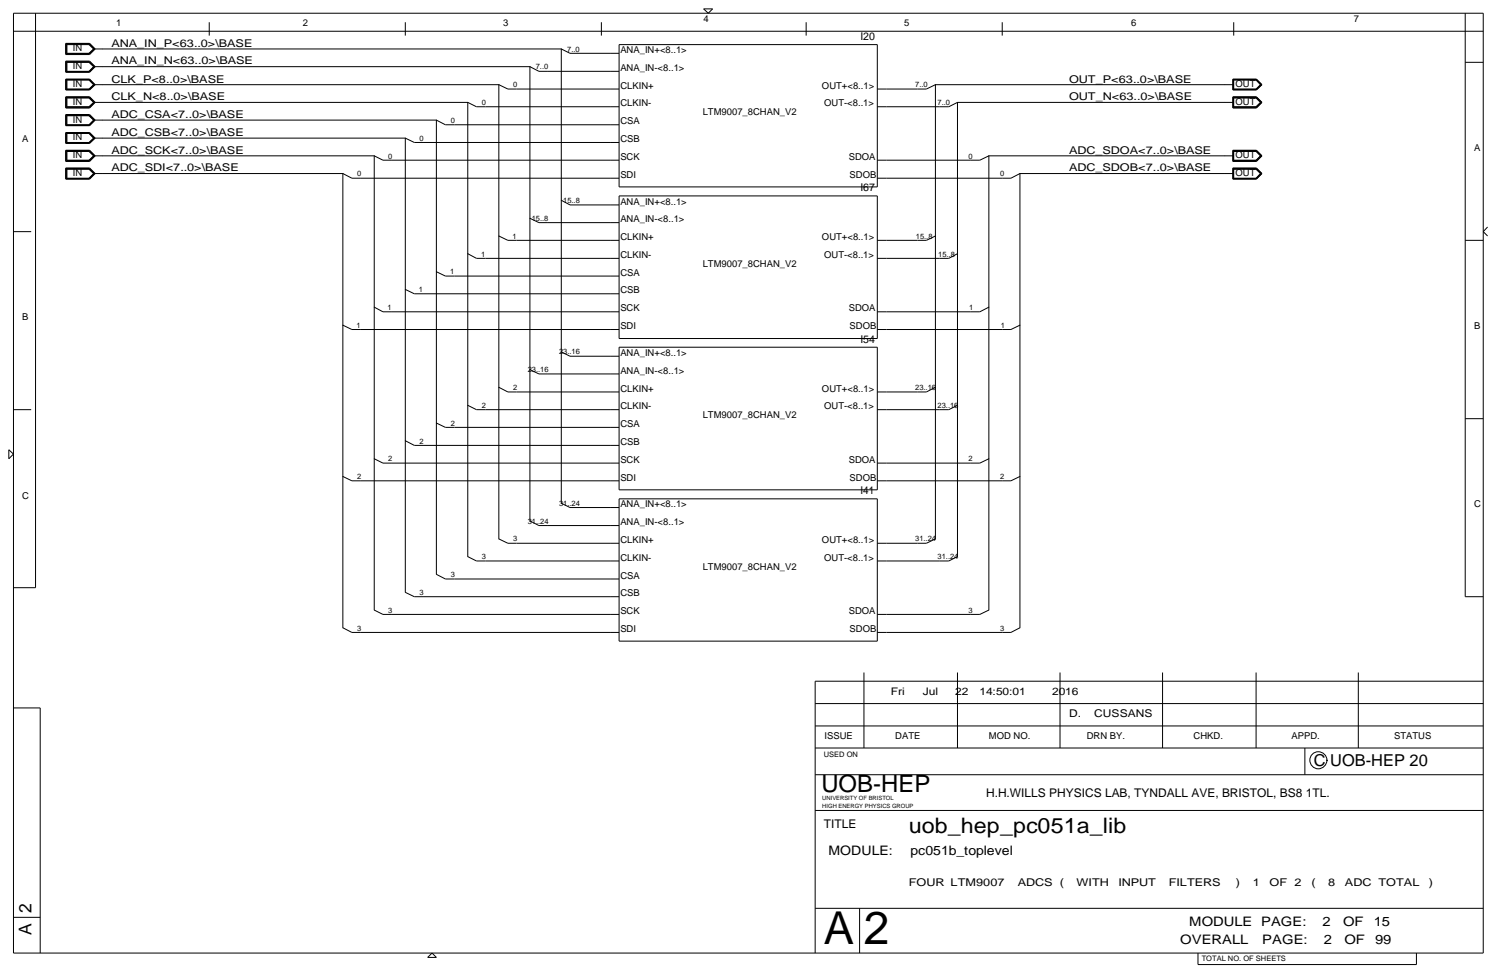
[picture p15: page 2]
FOUR LTM9007 ADCS ( WITH INPUT FILTERS; ) 1 OF 2 ( 8 ADC TOTAL ); uob_hep_pc051a_lib; ADC_SDI<7..0>\BASE; ADC_CSB<7..0>\BASE ADC_SCK<7..0>\BASE; CLK_N<8..0>\BASE; CLK_P<8..0>\BASE; ADC_CSA<7..0>\BASE; ANA_IN_N<63..0>\BASE; ANA_IN_P<63..0>\BASE; OUT_N<63..0>\BASE; ADC_SDOA<7..0>\BASE; OUT_P<63..0>\BASE; ADC_SDOB<7..0>\BASE; LTM9007_8CHAN_V2; ANA_IN+<8..1>; CLKIN+; ANA_IN-<8..1>; CLKIN-; CSA; CSB; SCK; SDI; SDOB; SDOA; OUT-<8..1>; OUT+<8..1>; OUT; UOB-HEP

Fri Jul | 22 14:50:01 2016

D. CUSSANS

ISSUE | DATE | MOD NO. | DRN BY. | CHKD. | APPD. | STATUS

USED ON | C UOB-HEP 20

H.H.WILLS PHYSICS LAB, TYNDALL AVE, BRISTOL, BS8 1TL.

UNIVERSITY OF BRISTOL
HIGH ENERGY PHYSICS GROUP
TITLE
MODULE: pc051b_toplevel

MODULE PAGE: 2 OF 15
OVERALL PAGE: 2 OF 99

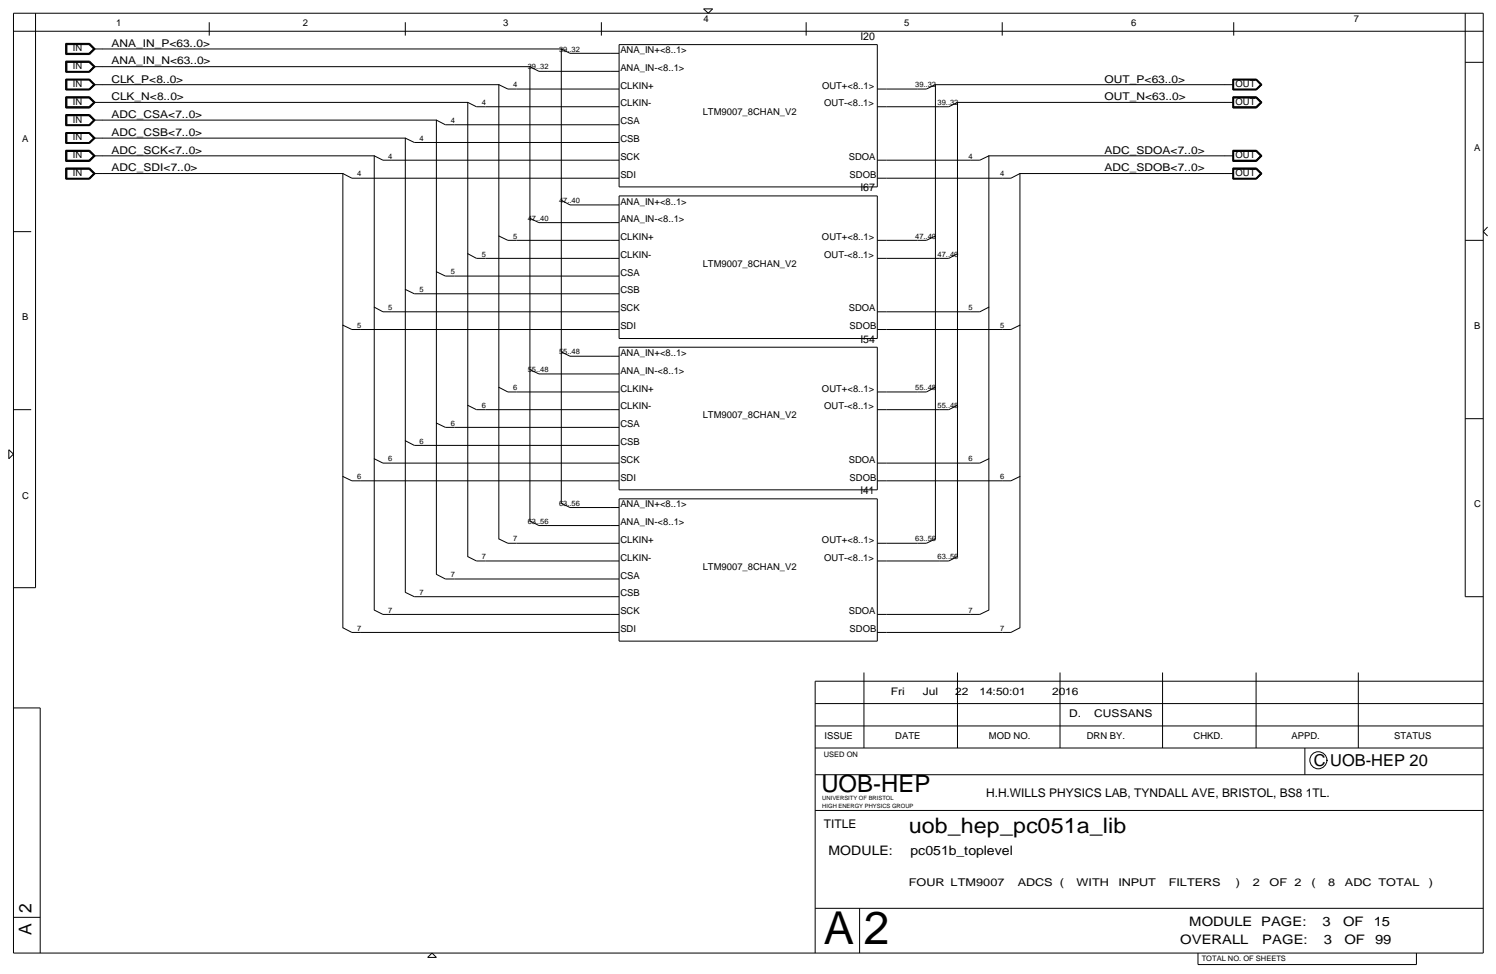
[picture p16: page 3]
FOUR LTM9007 ADCS ( WITH INPUT FILTERS; ) 2 OF 2 ( 8 ADC TOTAL ); uob_hep_pc051a_lib; CLK_P<8..0> CLK_N<8..0> ADC_CSA<7..0>; ANA_IN_N<63..0>; ANA_IN_P<63..0>; ADC_CSB<7..0> ADC_SCK<7..0> ADC_SDI<7..0>; OUT_N<63..0>; OUT_P<63..0>; ADC_SDOA<7..0> ADC_SDOB<7..0>; LTM9007_8CHAN_V2; ANA_IN+<8..1>; CLKIN+; ANA_IN-<8..1>; CLKIN-; CSA; CSB; SCK; SDI; SDOB; SDOA; OUT-<8..1>; OUT+<8..1>; OUT; UOB-HEP

Fri Jul | 22 14:50:01 2016

D. CUSSANS

ISSUE | DATE | MOD NO. | DRN BY. | CHKD. | APPD. | STATUS

USED ON | C UOB-HEP 20

H.H.WILLS PHYSICS LAB, TYNDALL AVE, BRISTOL, BS8 1TL.

UNIVERSITY OF BRISTOL
HIGH ENERGY PHYSICS GROUP
TITLE
MODULE: pc051b_toplevel

MODULE PAGE: 3 OF 15
OVERALL PAGE: 3 OF 99

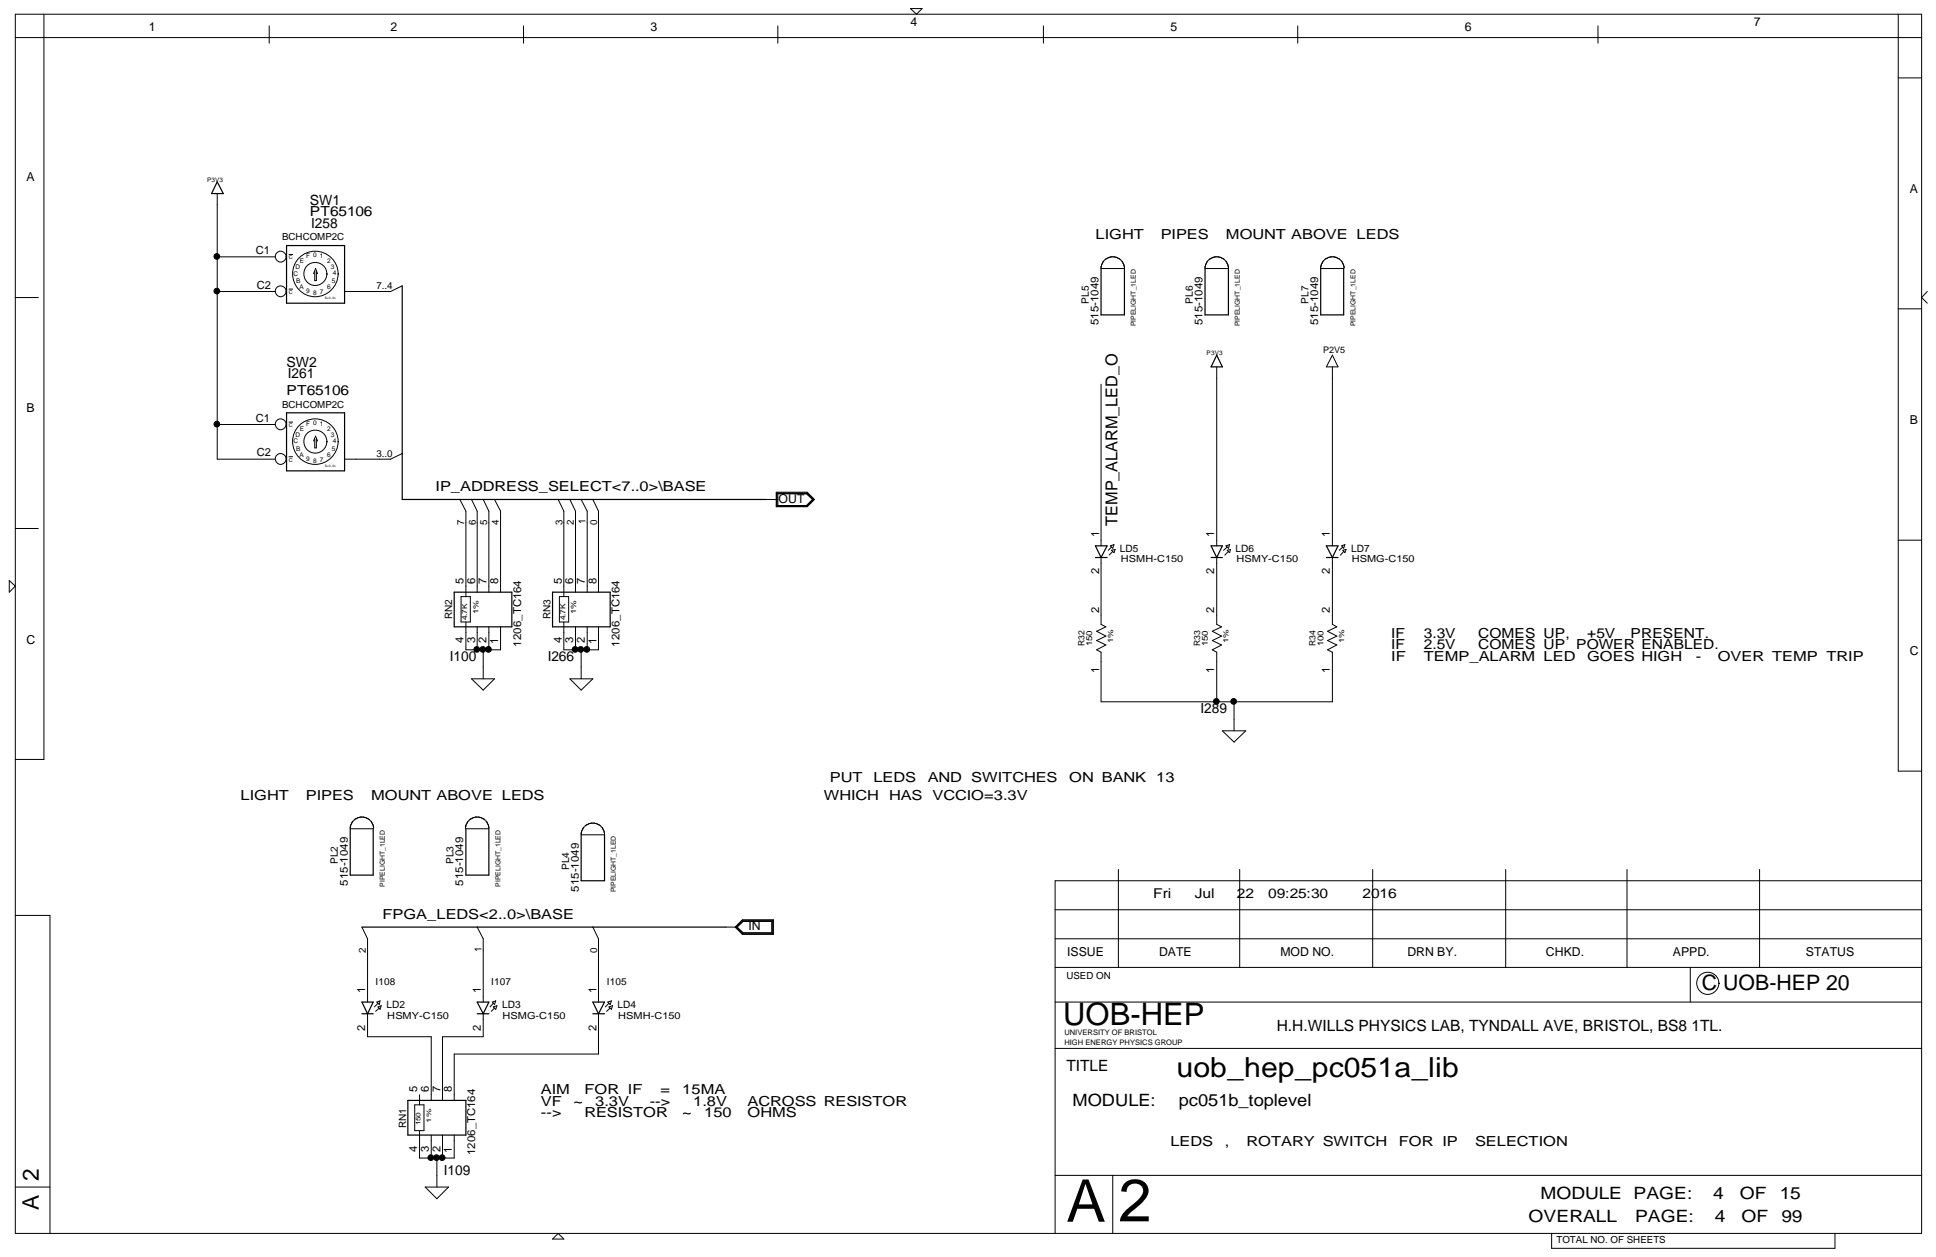
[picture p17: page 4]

LIGHT PIPES MOUNT ABOVE LEDS

IF TEMP_ALARM LED GOES HIGH - OVER TEMP TRIP

PUT LEDS AND SWITCHES ON BANK 13
WHICH HAS VCCIO=3.3V

ISSUE | DATE | MOD NO. | DRN BY. | CHKD. | APPD. | STATUS

USED ON | C UOB-HEP 20

H.H.WILLS PHYSICS LAB, TYNDALL AVE, BRISTOL, BS8 1TL.

LEDS , ROTARY SWITCH FOR IP SELECTION

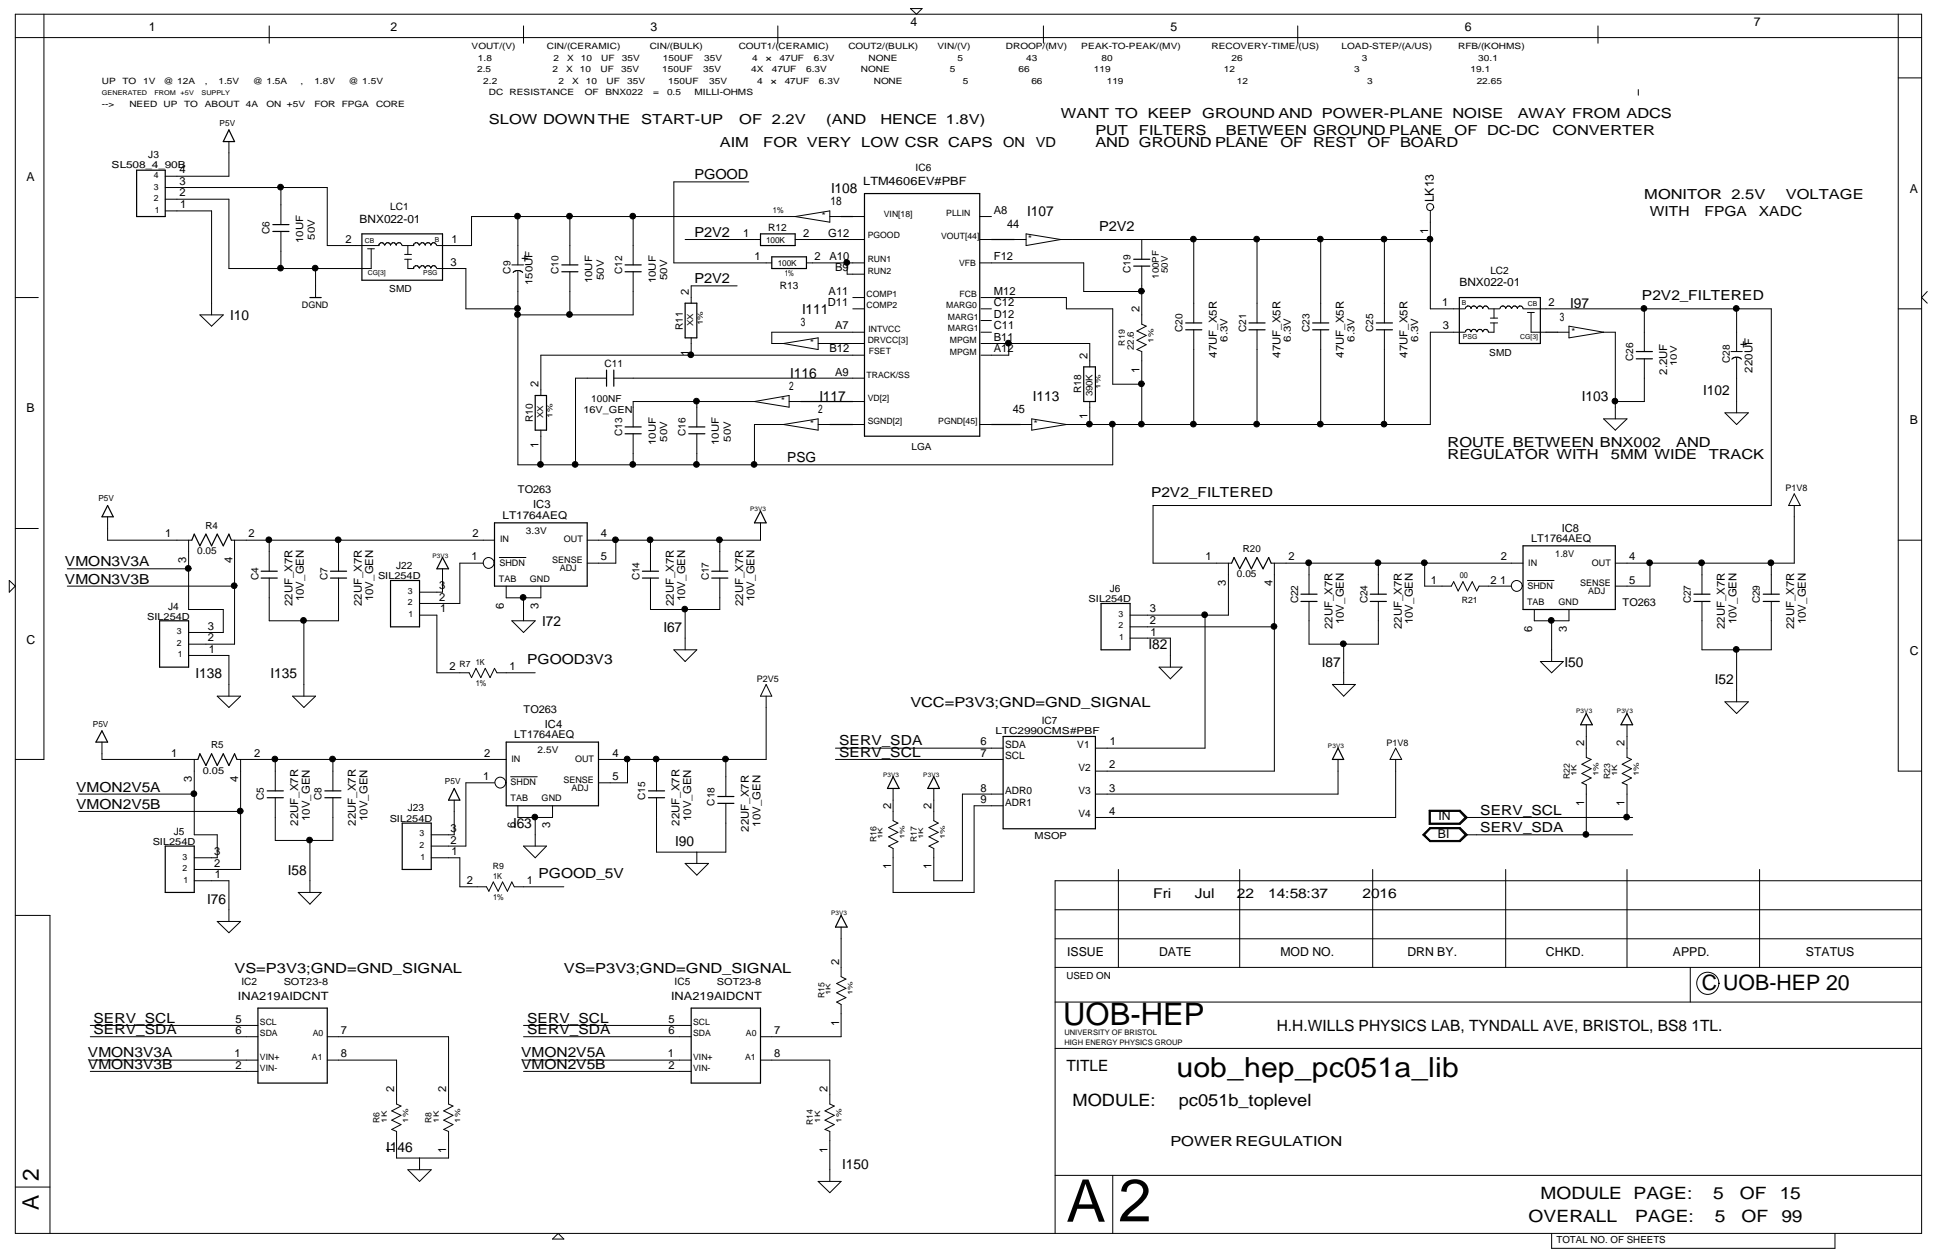
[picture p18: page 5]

WANT TO KEEP GROUND AND POWER-PLANE NOISE AWAY FROM ADCS
AND GROUND PLANE OF REST OF BOARD

AIM FOR VERY LOW CSR CAPS

ROUTE BETWEEN BNX002 AND
REGULATOR WITH 5MM WIDE TRACK

ISSUE | DATE | MOD NO. | DRN BY. | CHKD. | APPD. | STATUS

USED ON | C UOB-HEP 20

H.H.WILLS PHYSICS LAB, TYNDALL AVE, BRISTOL, BS8 1TL.

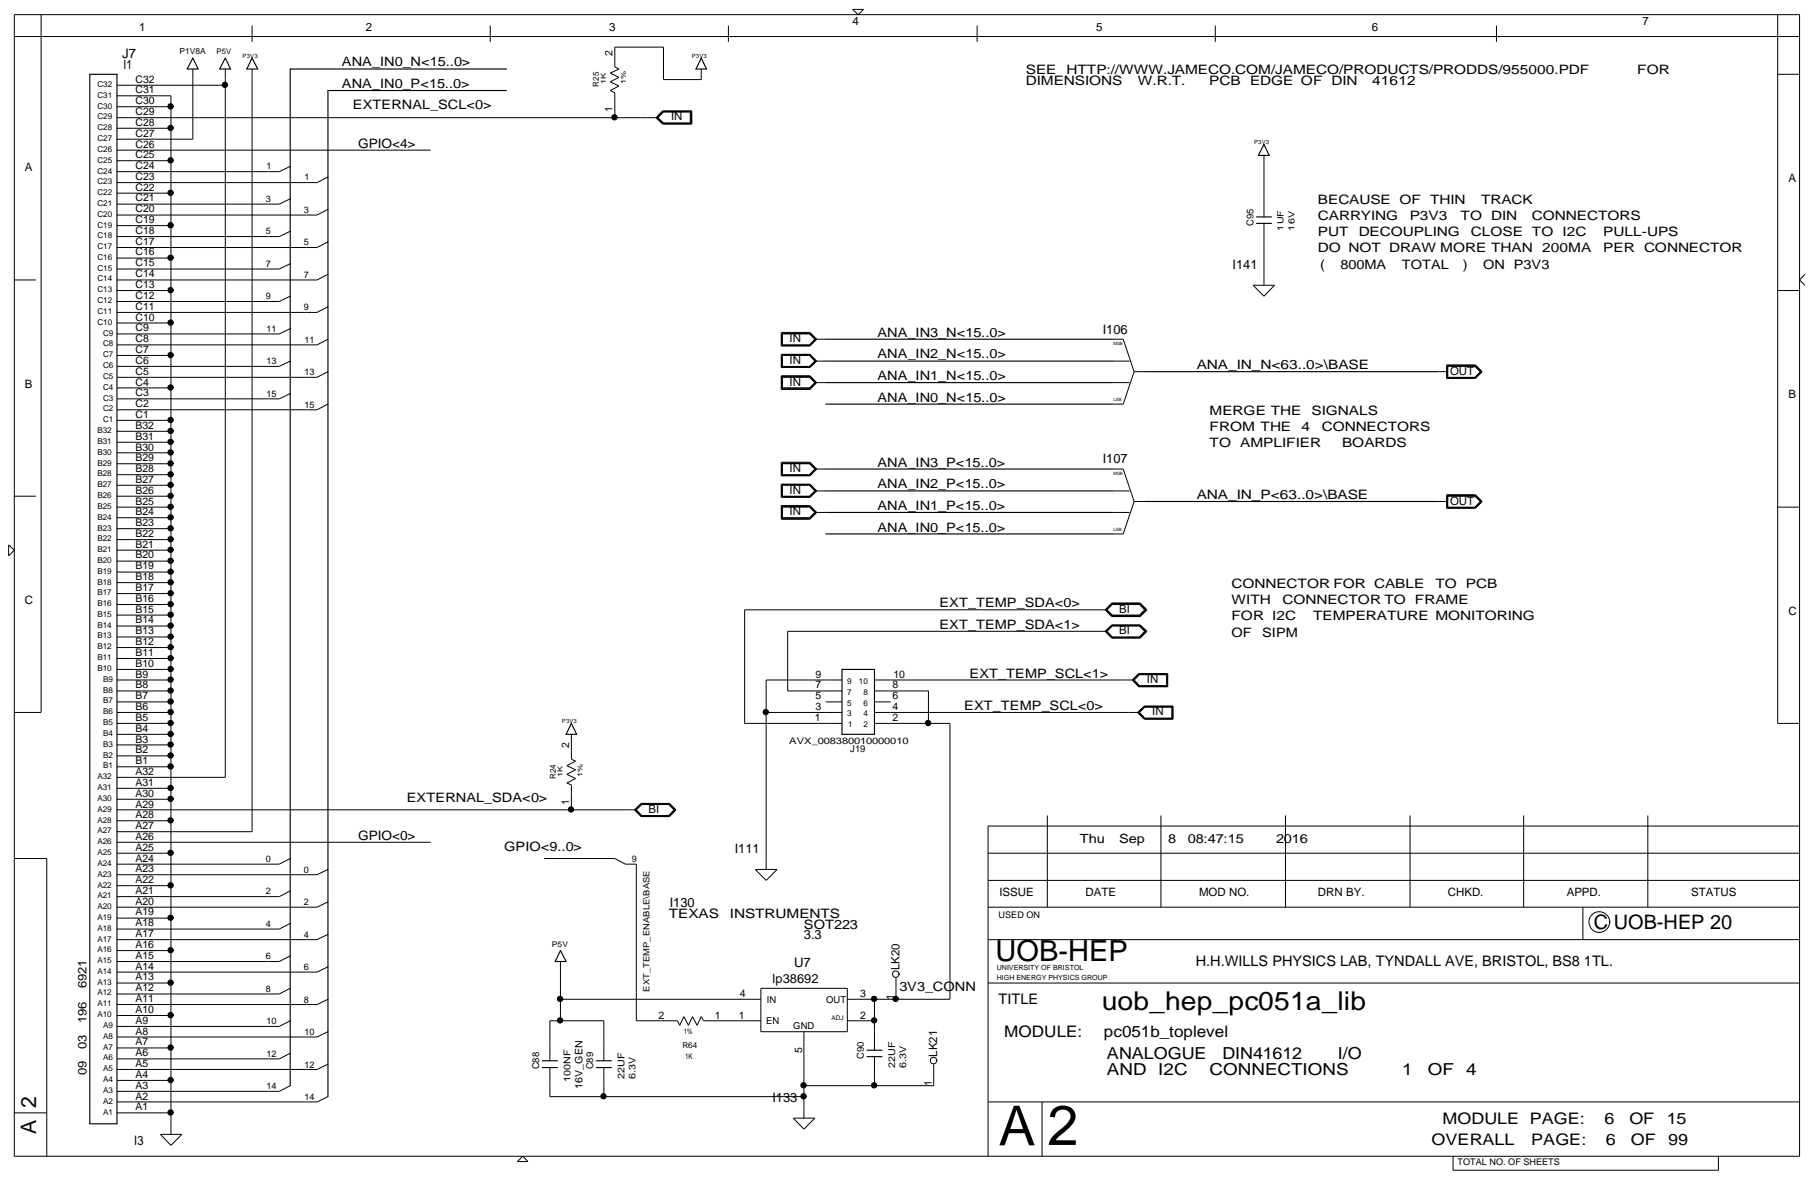
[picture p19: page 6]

BECAUSE OF THIN TRACK
CARRYING P3V3 TO DIN CONNECTORS
PUT DECOUPLING CLOSE TO I2C PULL-UPS
DO NOT DRAW MORE THAN 200MA PER CONNECTOR
( 800MA TOTAL ) ON P3V3

CONNECTOR FOR CABLE TO PCB
WITH CONNECTOR TO FRAME
FOR I2C TEMPERATURE MONITORING
OF SIPM

Thu Sep | 8 08:47:15 2016

ISSUE | DATE | MOD NO. | DRN BY. | CHKD. | APPD. | STATUS

USED ON | C UOB-HEP 20

H.H.WILLS PHYSICS LAB, TYNDALL AVE, BRISTOL, BS8 1TL.

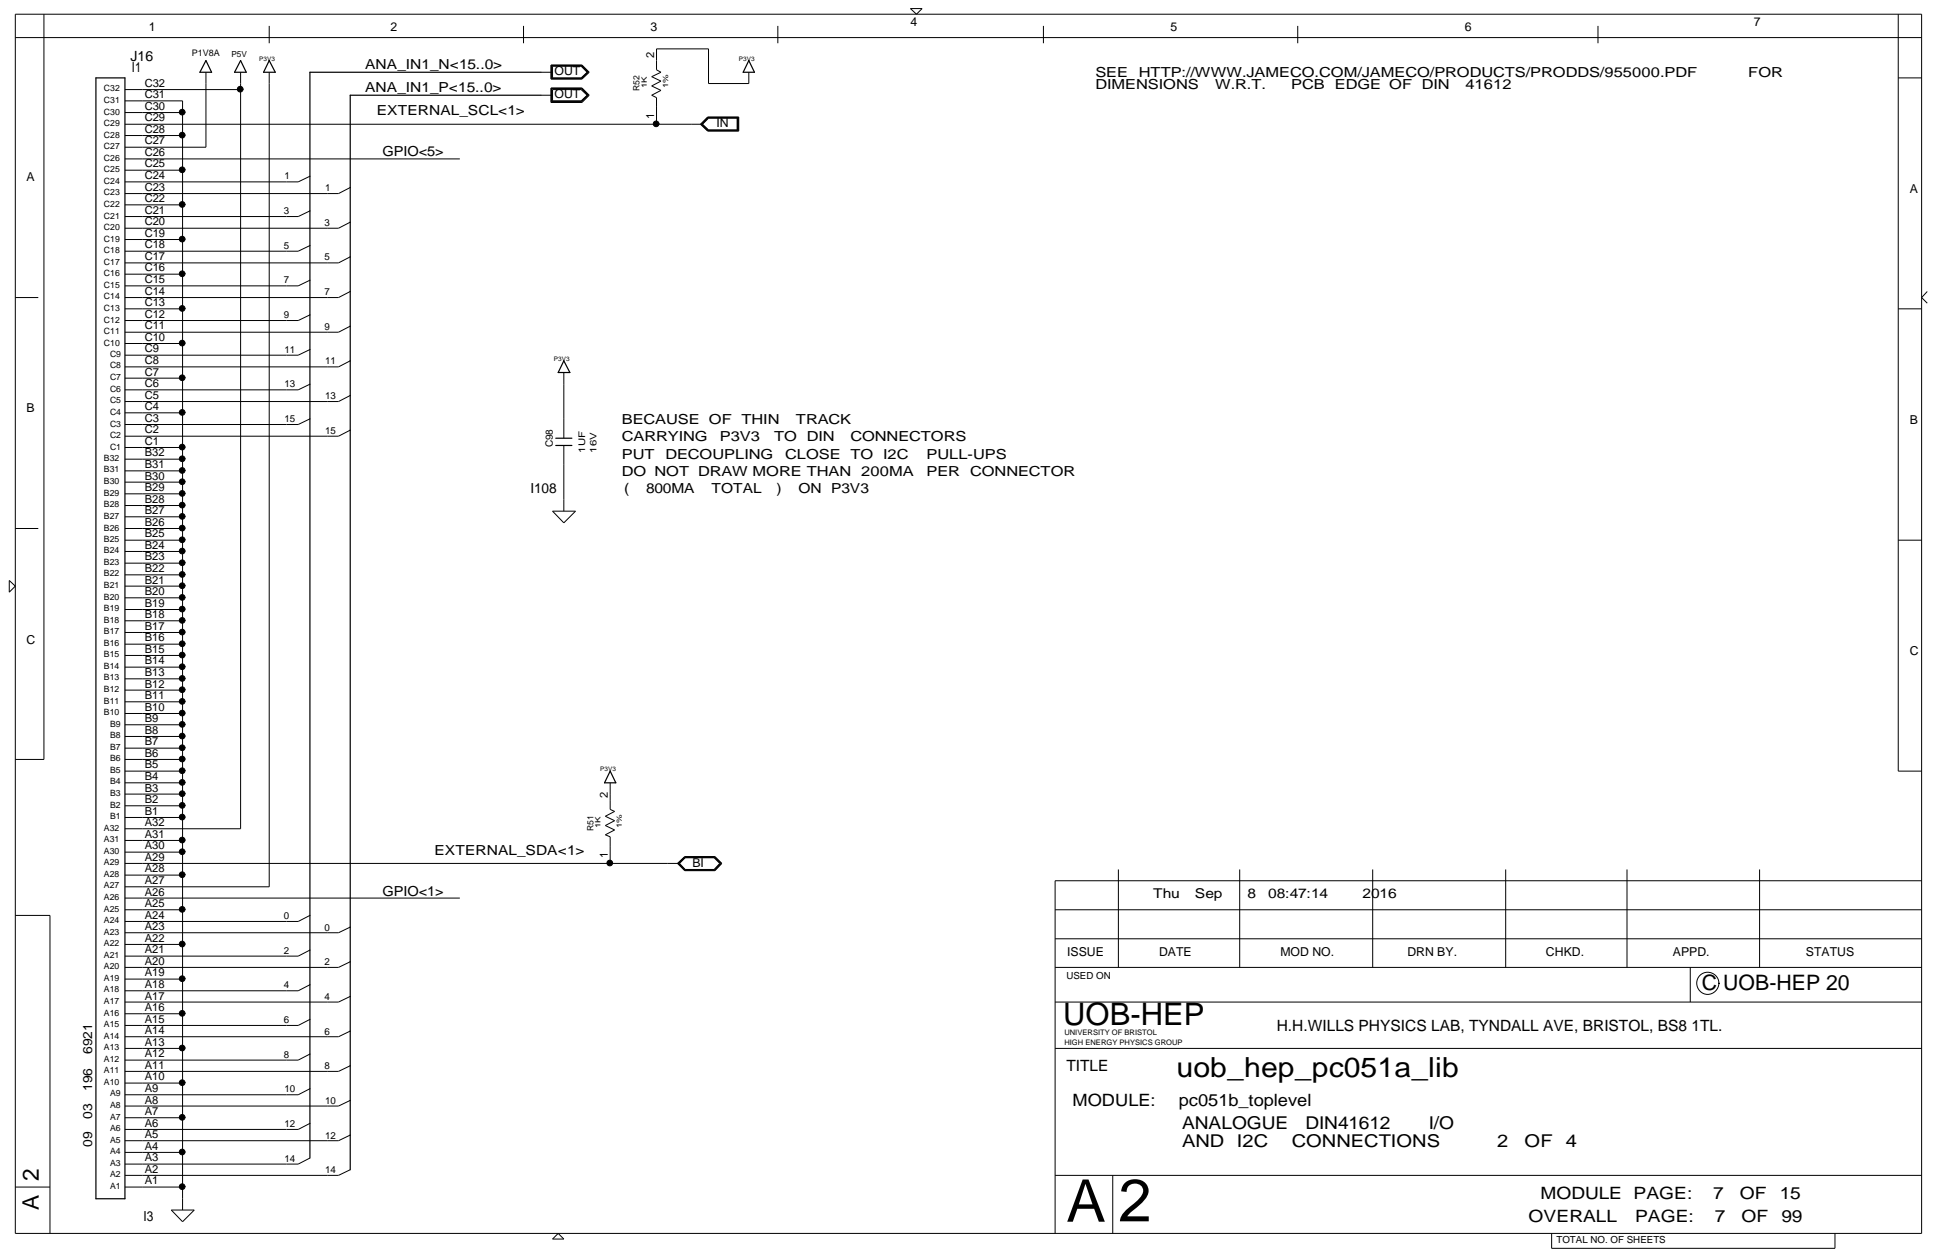
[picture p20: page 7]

BECAUSE OF THIN TRACK
CARRYING P3V3 TO DIN CONNECTORS
PUT DECOUPLING CLOSE TO I2C PULL-UPS
DO NOT DRAW MORE THAN 200MA PER CONNECTOR
( 800MA TOTAL ) ON P3V3

ISSUE | DATE | MOD NO. | DRN BY. | CHKD. | APPD. | STATUS

USED ON | C UOB-HEP 20

H.H.WILLS PHYSICS LAB, TYNDALL AVE, BRISTOL, BS8 1TL.

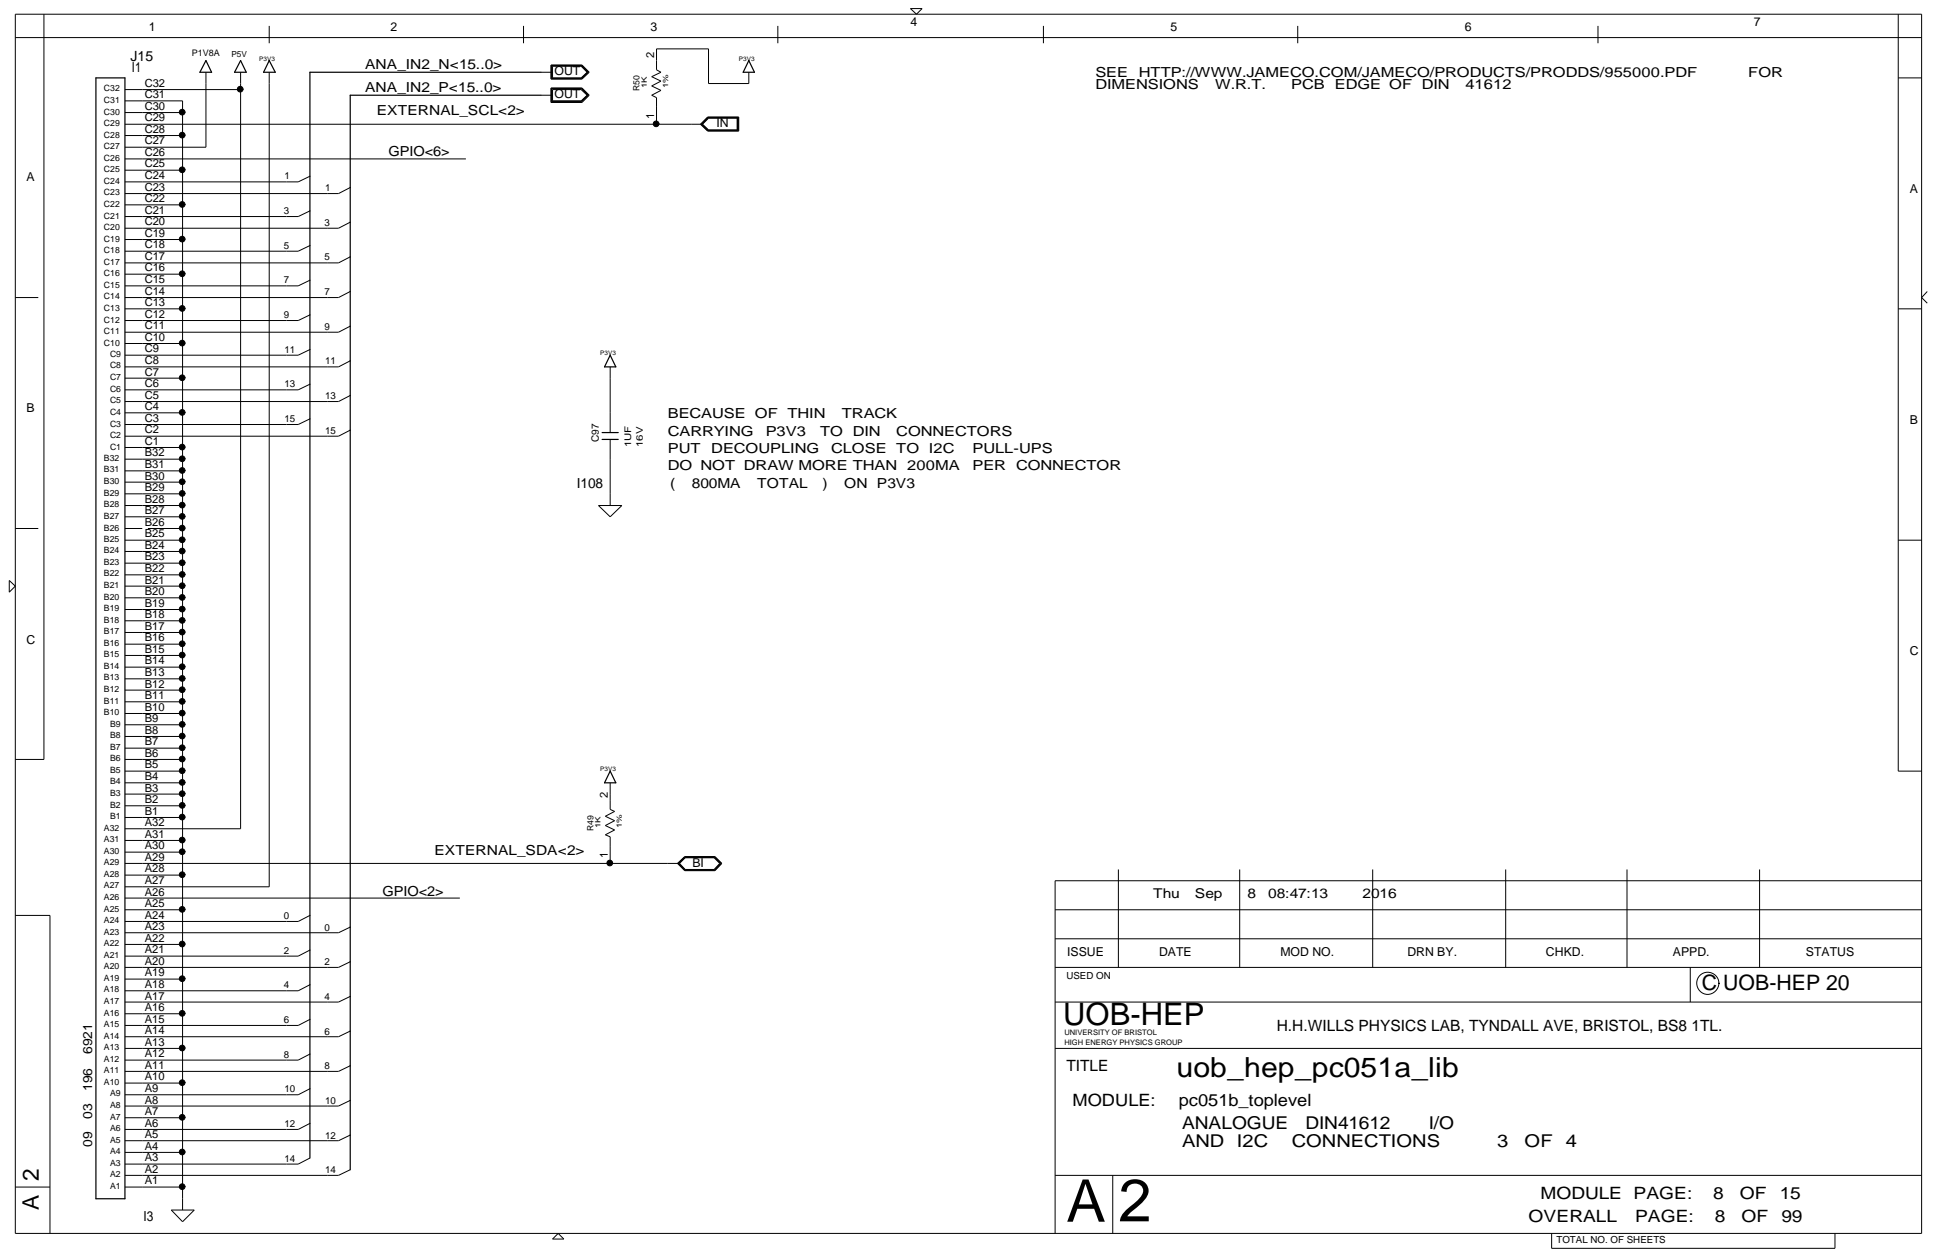
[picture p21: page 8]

BECAUSE OF THIN TRACK
CARRYING P3V3 TO DIN CONNECTORS
PUT DECOUPLING CLOSE TO I2C PULL-UPS
DO NOT DRAW MORE THAN 200MA PER CONNECTOR
( 800MA TOTAL ) ON P3V3

ISSUE | DATE | MOD NO. | DRN BY. | CHKD. | APPD. | STATUS

USED ON | C UOB-HEP 20

H.H.WILLS PHYSICS LAB, TYNDALL AVE, BRISTOL, BS8 1TL.

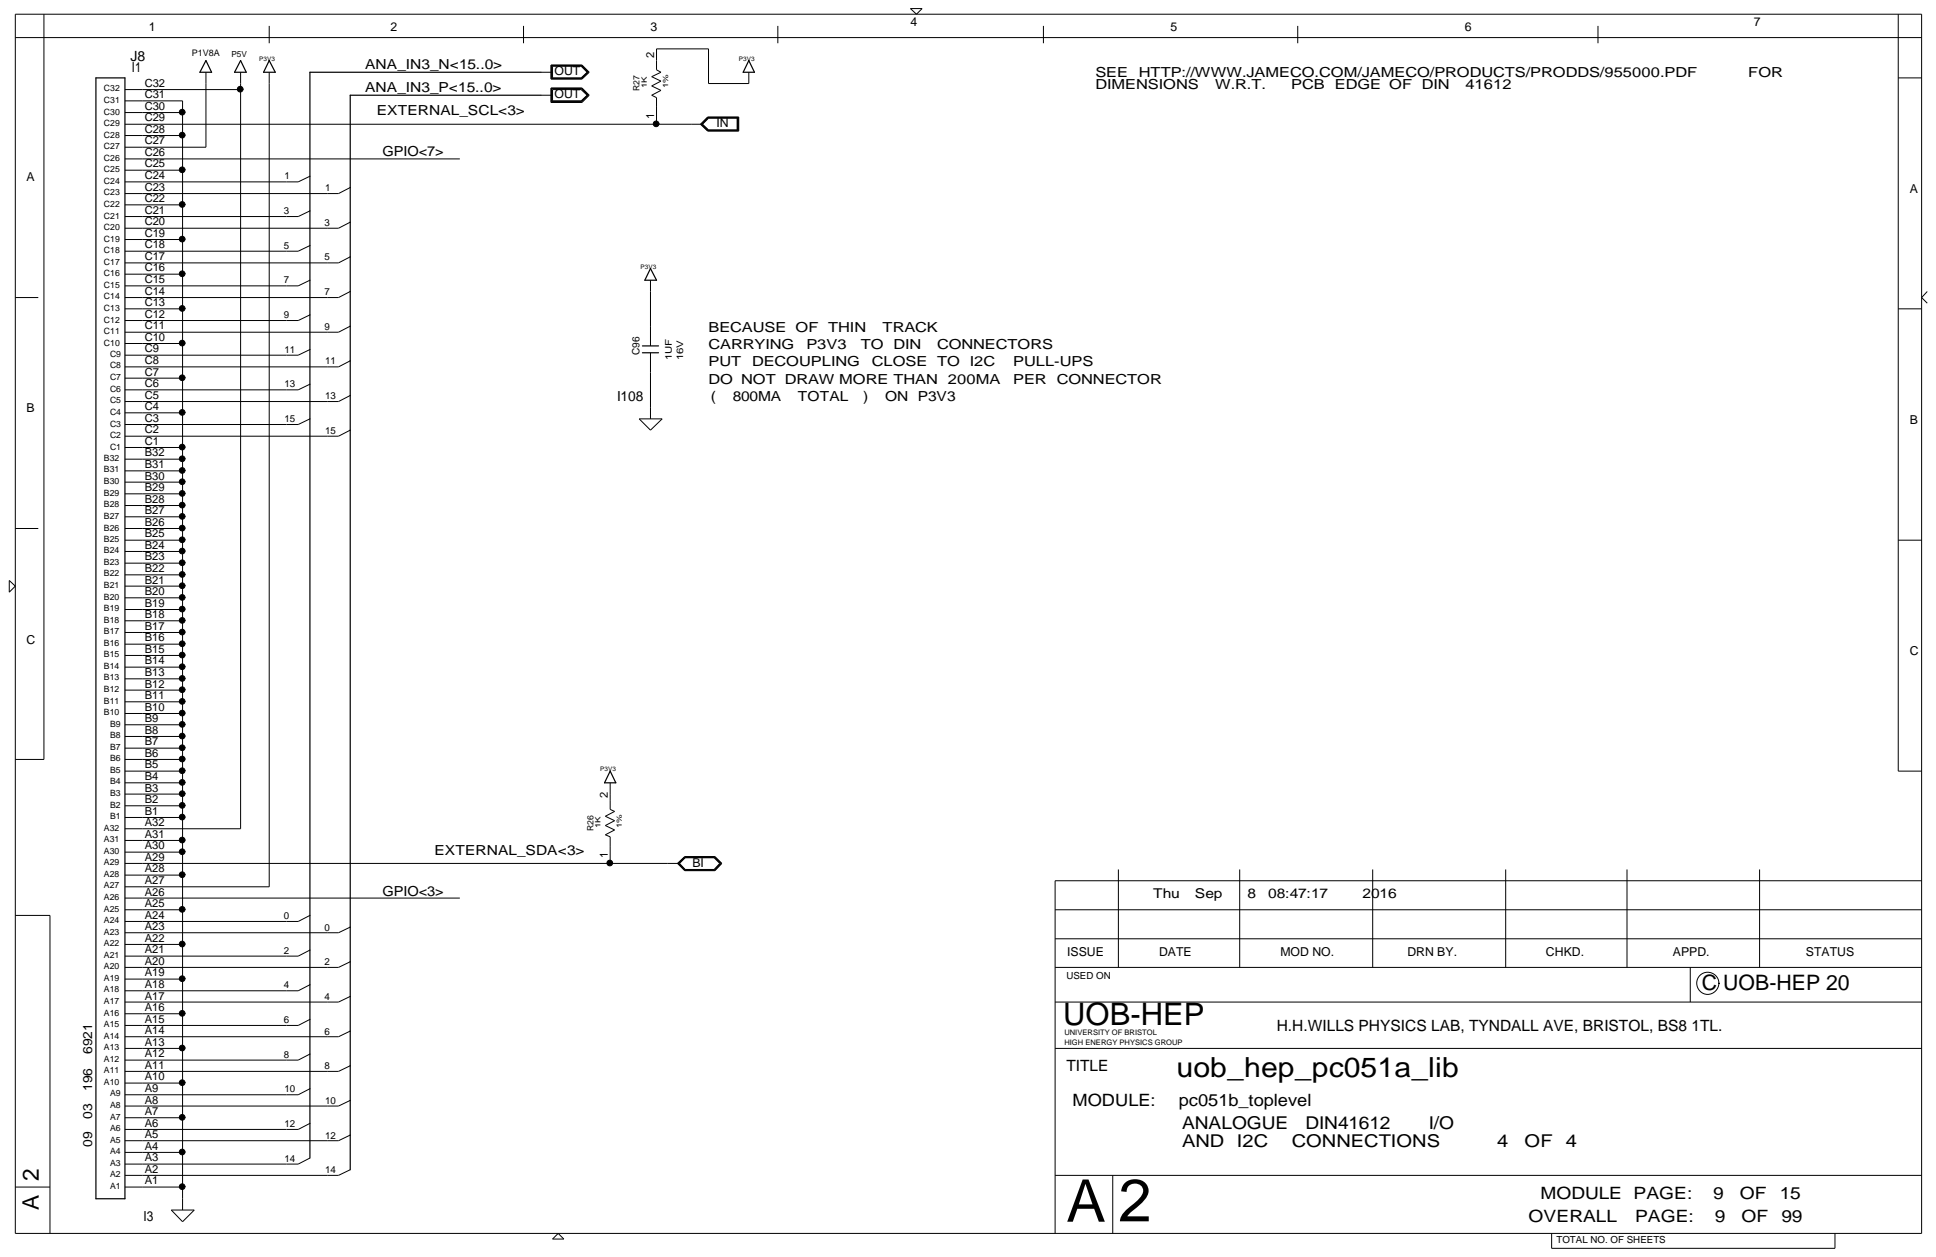
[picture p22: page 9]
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

ISSUE | DATE | MOD NO. | DRN BY. | CHKD. | APPD. | STATUS

USED ON | C UOB-HEP 20

H.H.WILLS PHYSICS LAB, TYNDALL AVE, BRISTOL, BS8 1TL.

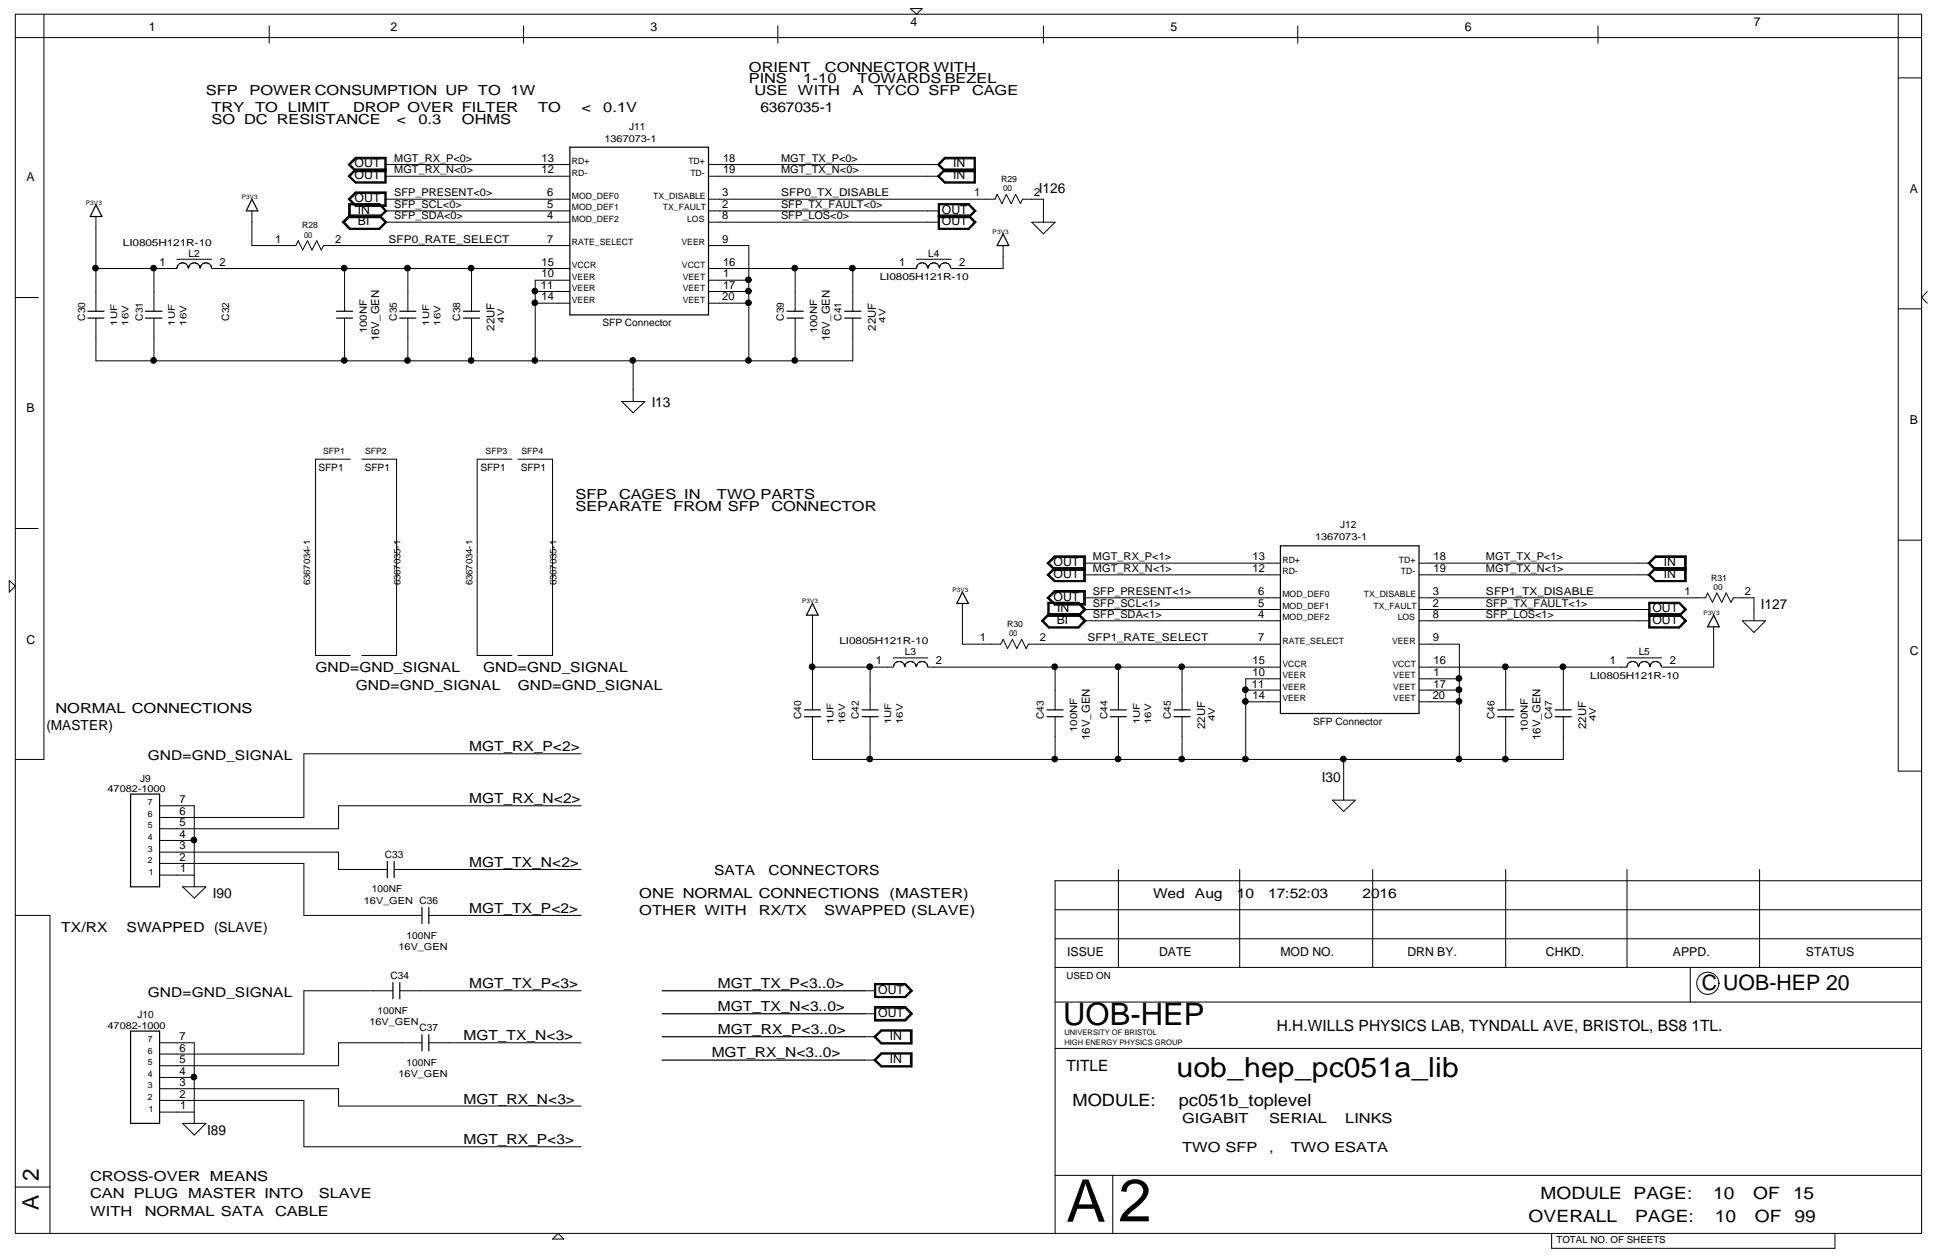
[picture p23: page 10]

ORIENT CONNECTOR WITH
USE WITH A TYCO SFP CAGE

SFP POWER CONSUMPTION UP TO 1W

11 | 17
14 | 20

SFP CAGES IN TWO PARTS
SEPARATE FROM SFP CONNECTOR

IN SFP_SDA<1> 4 | 8 SFP_LOS<1> | OUT

10

ONE NORMAL CONNECTIONS (MASTER)
OTHER WITH RX/TX SWAPPED (SLAVE)

Wed Aug 10 17:52:03 | 2016

ISSUE | DATE | MOD NO. | DRN BY. | CHKD. | APPD. | STATUS

USED ON | C UOB-HEP 20

H.H.WILLS PHYSICS LAB, TYNDALL AVE, BRISTOL, BS8 1TL.

UNIVERSITY OF BRISTOL
HIGH ENERGY PHYSICS GROUP
TITLE
MODULE: pc051b_toplevel

TWO SFP , TWO ESATA

CROSS-OVER MEANS
CAN PLUG MASTER INTO SLAVE
WITH NORMAL SATA CABLE

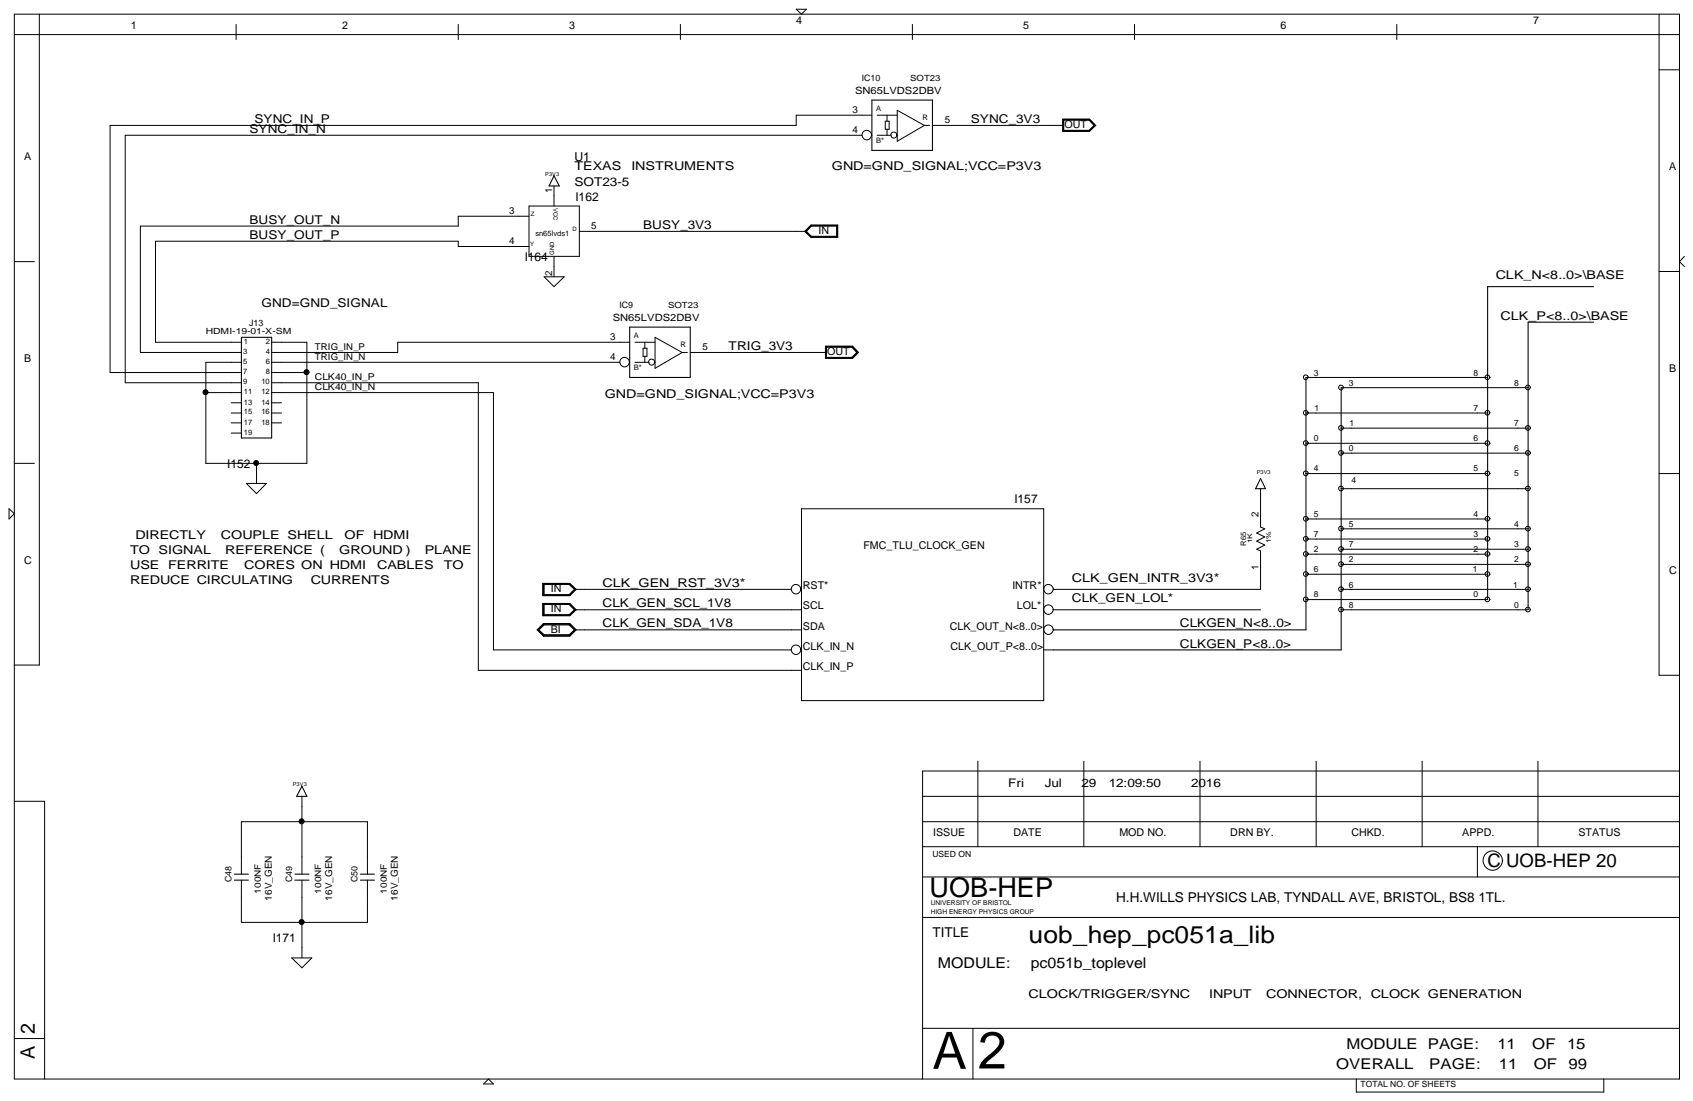
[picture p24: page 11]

IC10 SOT23 SN65LVDS2DBV

CLK40_IN_N

DIRECTLY COUPLE SHELL OF HDMI
TO SIGNAL REFERENCE ( GROUND ) PLANE
USE FERRITE CORES ON HDMI CABLES TO

ISSUE | DATE | MOD NO. | DRN BY. | CHKD. | APPD. | STATUS

USED ON | C UOB-HEP 20

H.H.WILLS PHYSICS LAB, TYNDALL AVE, BRISTOL, BS8 1TL.

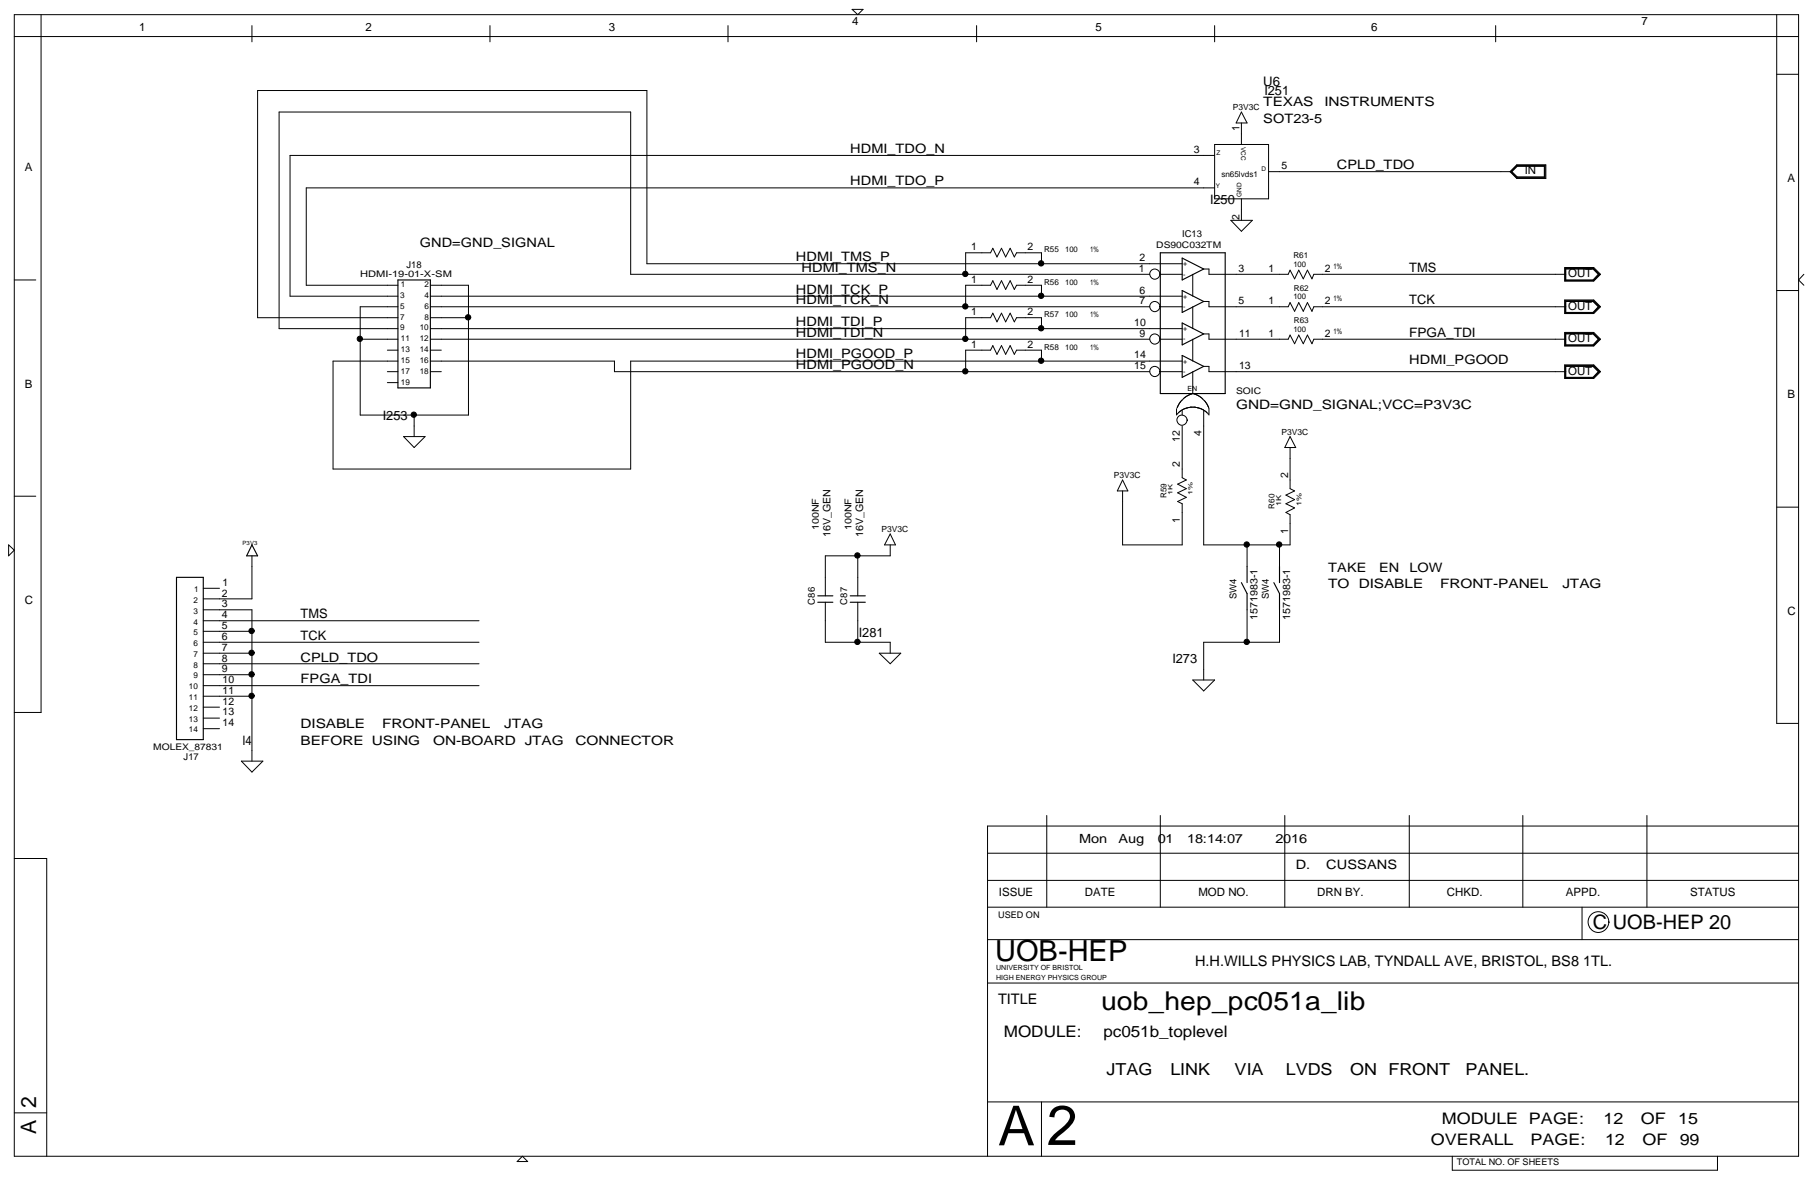
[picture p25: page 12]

HDMI_TDO_P 4

TAKE EN LOW
TO DISABLE FRONT-PANEL JTAG

DISABLE FRONT-PANEL JTAG
BEFORE USING ON-BOARD JTAG CONNECTOR

Mon Aug 01 18:14:07 | 2016

D. CUSSANS

ISSUE | DATE | MOD NO. | DRN BY. | CHKD. | APPD. | STATUS

USED ON | C UOB-HEP 20

H.H.WILLS PHYSICS LAB, TYNDALL AVE, BRISTOL, BS8 1TL.

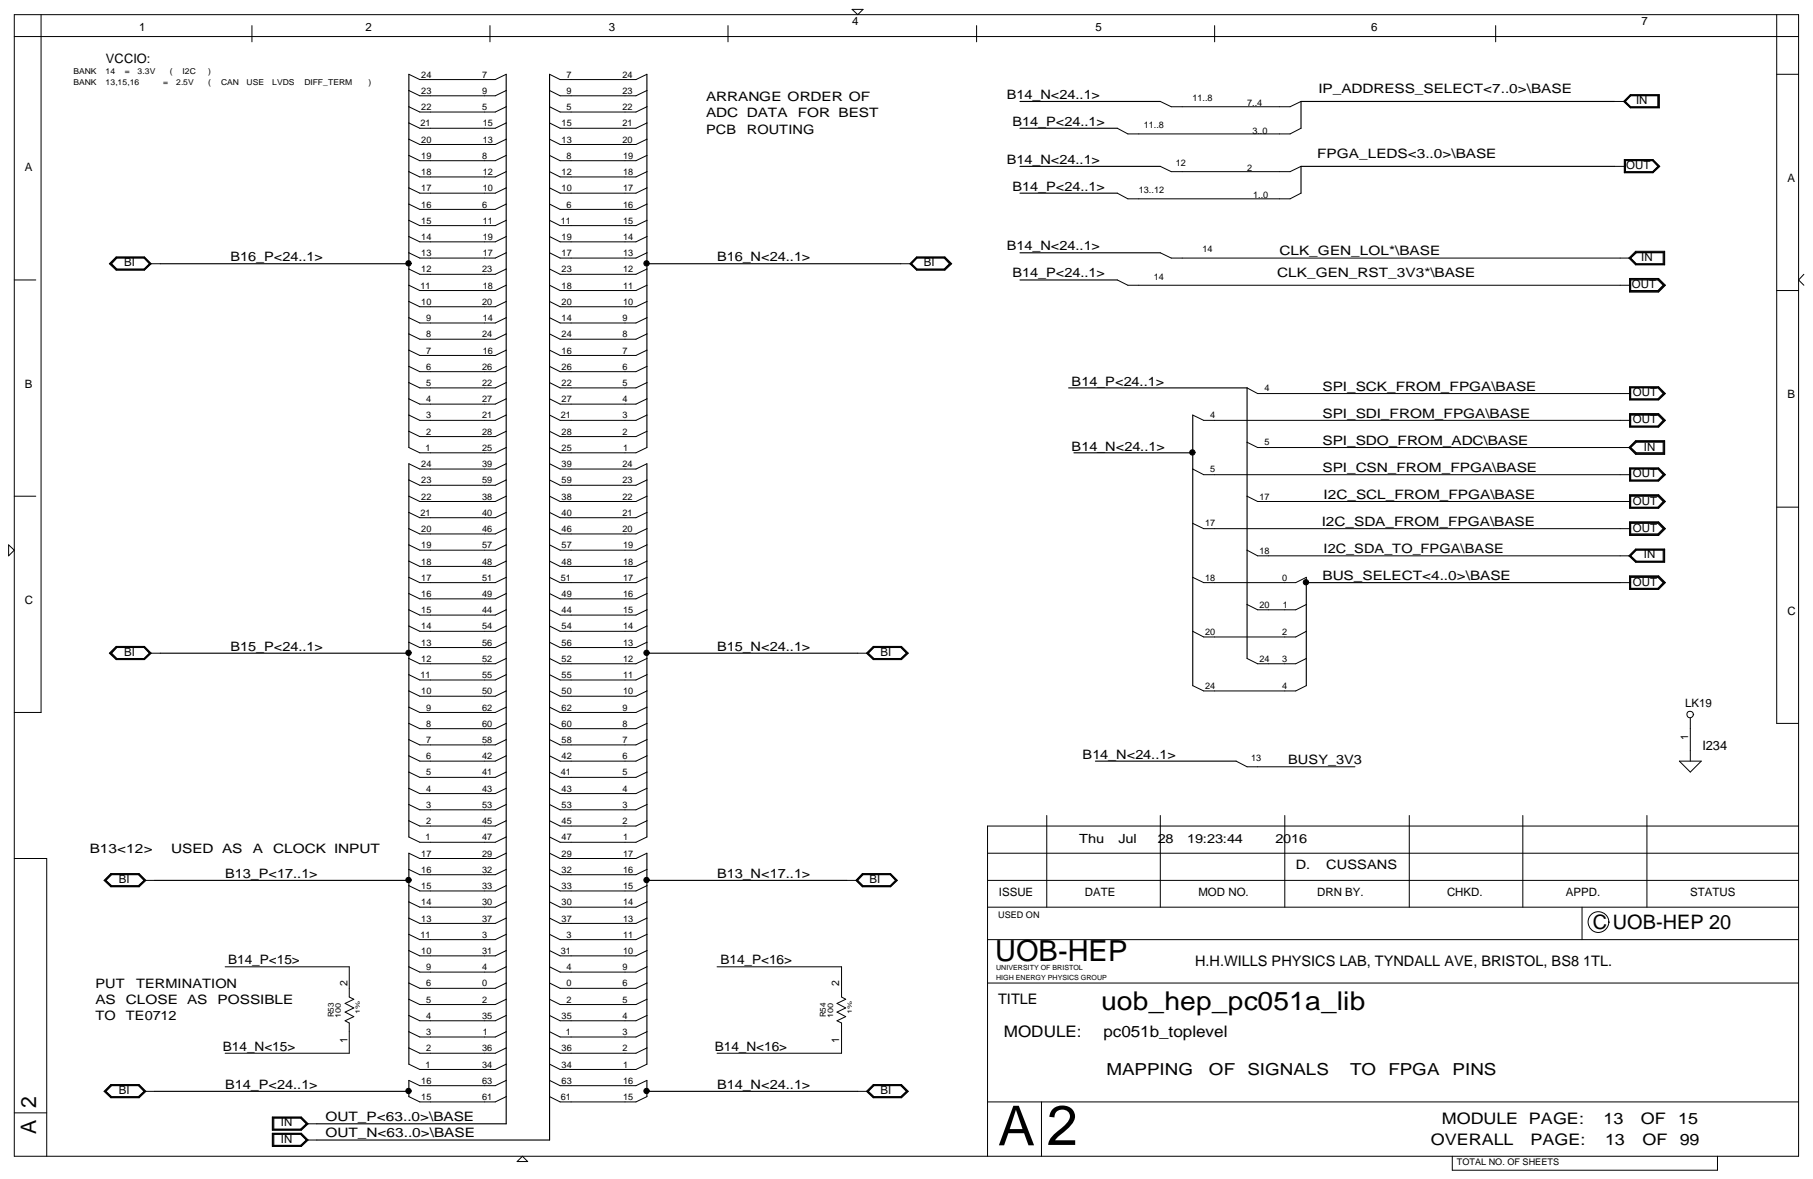
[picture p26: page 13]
BANK 13,15,16; ( CAN USE LVDS DIFF_TERM; BANK 14 = 3.3V; VCCIO:; USED AS A CLOCK INPUT; uob_hep_pc051a_lib; BUSY_3V3 B14_N<24..1>; CLK_GEN_RST_3V3*\BASE; I2C_SCL_FROM_FPGA\BASE; I2C_SDA_FROM_FPGA\BASE; CLK_GEN_LOL*\BASE; SPI_SCK_FROM_FPGA\BASE; SPI_SDI_FROM_FPGA\BASE; SPI_CSN_FROM_FPGA\BASE; I2C_SDA_TO_FPGA\BASE; SPI_SDO_FROM_ADC\BASE; BUS_SELECT<4..0>\BASE; FPGA_LEDS<3..0>\BASE; IP_ADDRESS_SELECT<7..0>\BASE; OUT_P<63..0>\BASE OUT_N<63..0>\BASE; OUT; UOB-HEP

ARRANGE ORDER OF
ADC DATA FOR BEST
PCB ROUTING

Thu Jul | 28 19:23:44 2016

D. CUSSANS

ISSUE | DATE | MOD NO. | DRN BY. | CHKD. | APPD. | STATUS

USED ON | C UOB-HEP 20

H.H.WILLS PHYSICS LAB, TYNDALL AVE, BRISTOL, BS8 1TL.

UNIVERSITY OF BRISTOL
HIGH ENERGY PHYSICS GROUP
TITLE
MODULE: pc051b_toplevel

PUT TERMINATION
AS CLOSE AS POSSIBLE

MAPPING OF SIGNALS TO FPGA PINS

MODULE PAGE: 13 OF 15
OVERALL PAGE: 13 OF 99

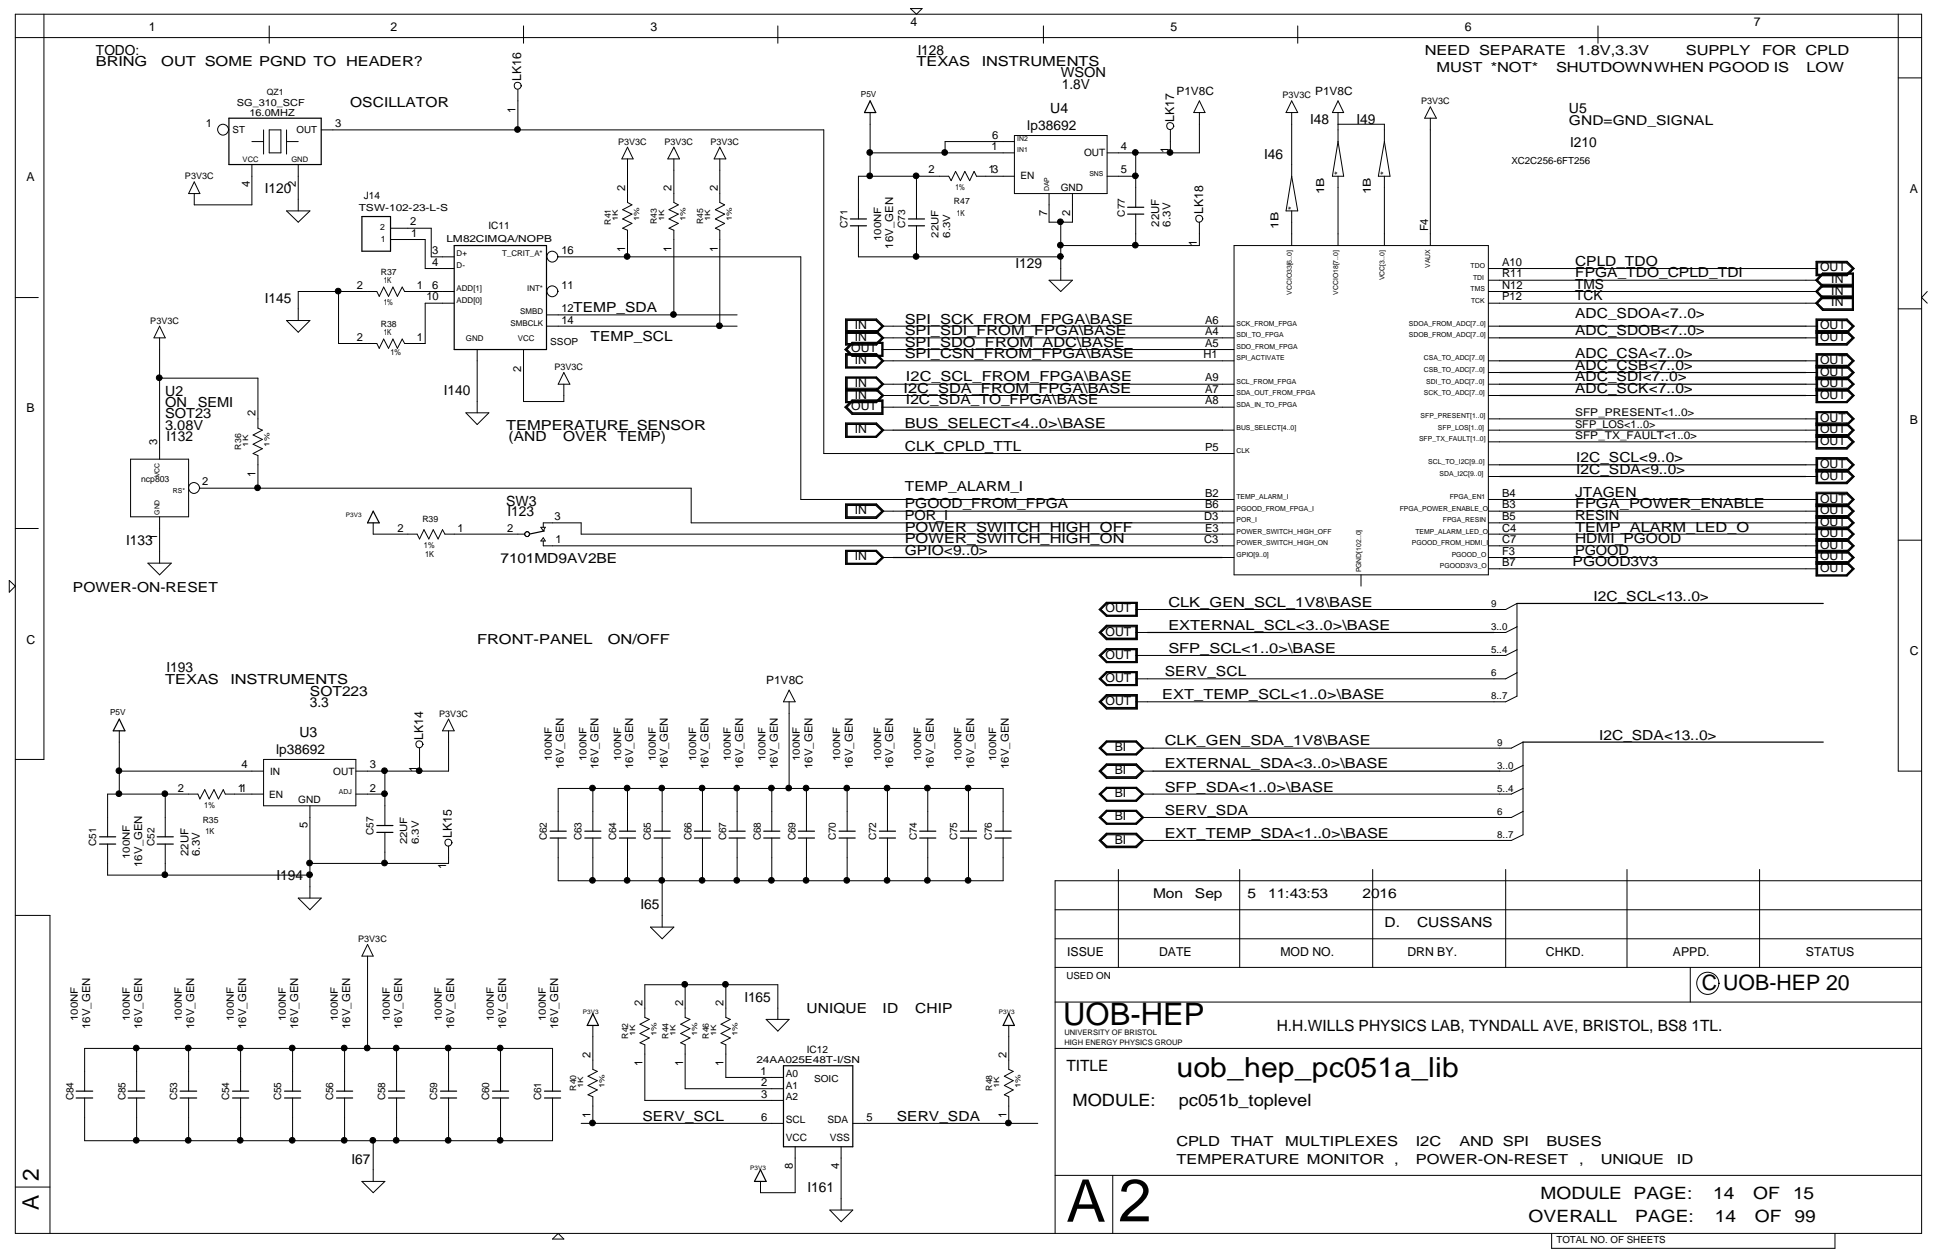
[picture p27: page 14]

FRONT-PANEL ON/OFF

Mon Sep | 5 11:43:53 2016

D. CUSSANS

ISSUE | DATE | MOD NO. | DRN BY. | CHKD. | APPD. | STATUS

USED ON | C UOB-HEP 20

H.H.WILLS PHYSICS LAB, TYNDALL AVE, BRISTOL, BS8 1TL.

CPLD THAT MULTIPLEXES I2C AND SPI BUSES
TEMPERATURE MONITOR , POWER-ON-RESET , UNIQUE ID

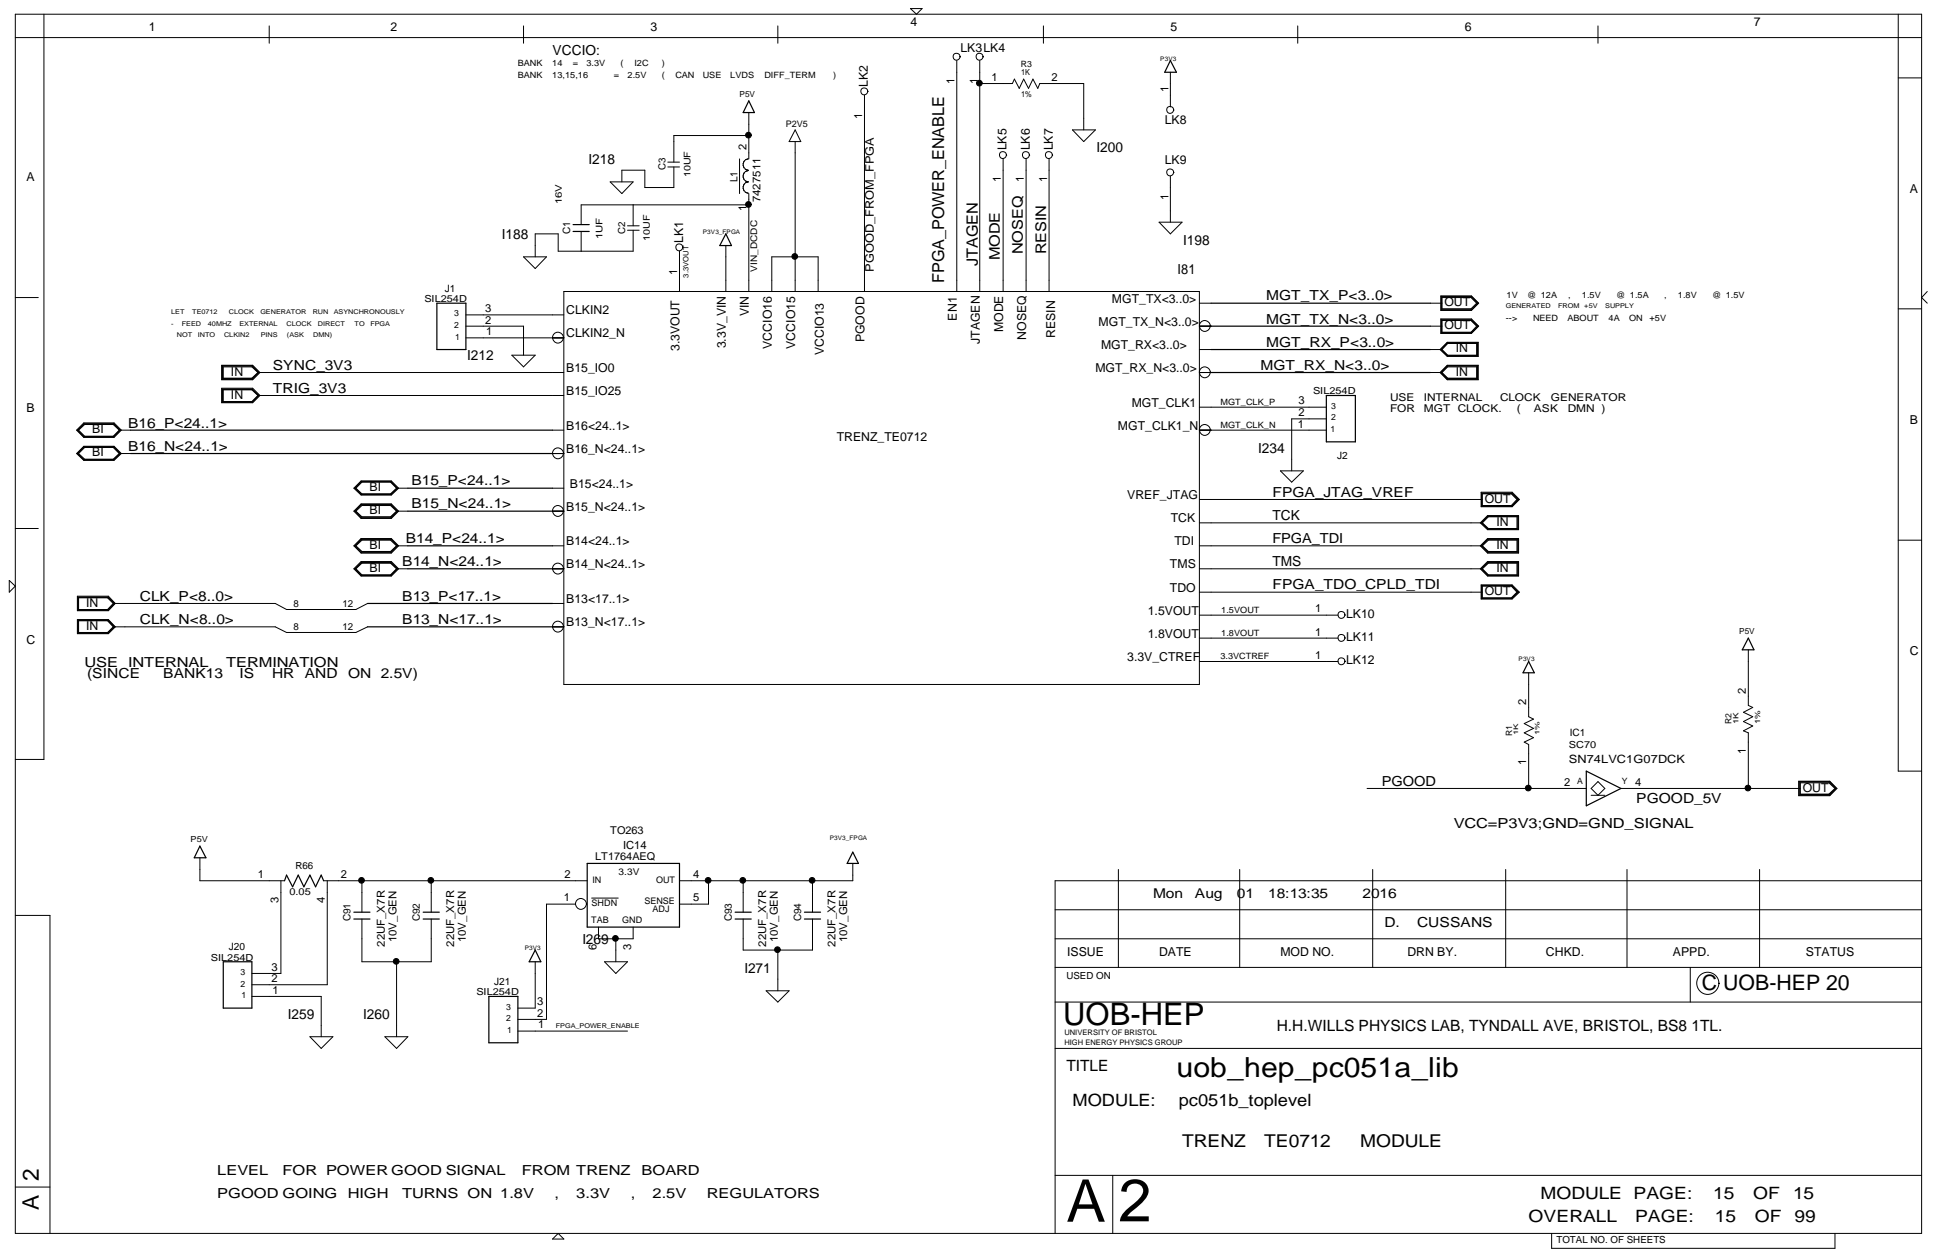
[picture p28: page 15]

Mon Aug 01 18:13:35 | 2016

D. CUSSANS

ISSUE | DATE | MOD NO. | DRN BY. | CHKD. | APPD. | STATUS

USED ON | C UOB-HEP 20

H.H.WILLS PHYSICS LAB, TYNDALL AVE, BRISTOL, BS8 1TL.

LEVEL FOR POWER GOOD SIGNAL FROM TRENZ BOARD

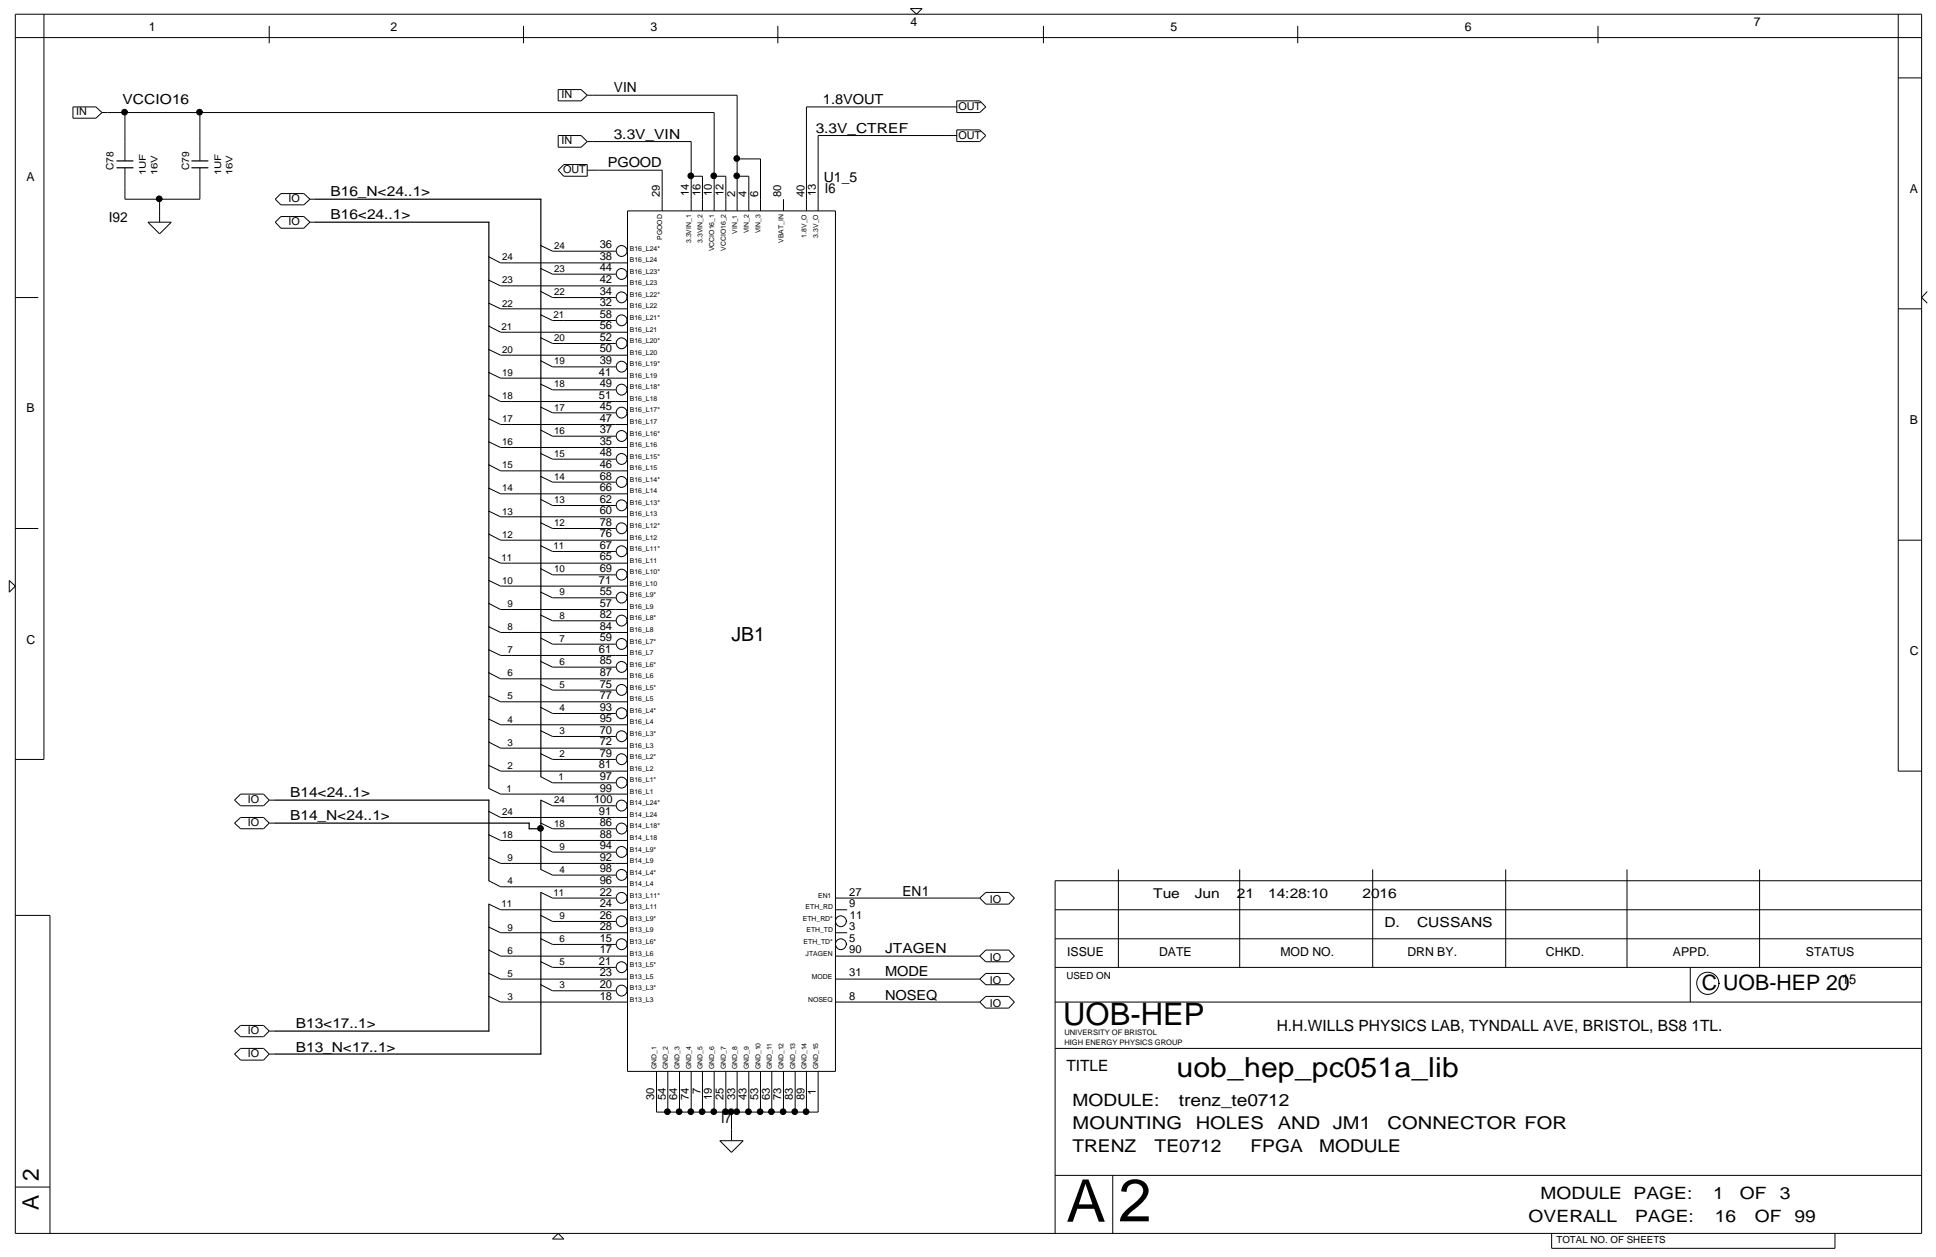
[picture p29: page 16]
TRENZ TE0712; FPGA MODULE; uob_hep_pc051a_lib; VCCIO16; PGOOD; 3.3V_VIN; NOSEQ; MODE; JTAGEN; VIN; 1.8VOUT; 3.3V_CTREF; ETH_TD*; ETH_TD; ETH_RD*; ETH_RD; VIN_1; VIN_2; VIN_3; VCCIO16_1; VCCIO16_2; VBAT_IN; GND_1; GND_2; GND_3; GND_4; GND_5; GND_6; GND_7; GND_8; GND_9; GND_10; GND_11; GND_12; GND_13; GND_14; GND_15; 3.3VIN_1; 3.3VIN_2; OUT; UOB-HEP

Tue Jun 21 14:28:10 | 2016

D. CUSSANS

ISSUE | DATE | MOD NO. | DRN BY. | CHKD. | APPD. | STATUS
USED ON | C UOB-HEP 20 15

H.H.WILLS PHYSICS LAB, TYNDALL AVE, BRISTOL, BS8 1TL.

UNIVERSITY OF BRISTOL
HIGH ENERGY PHYSICS GROUP
TITLE

MODULE: trenz_te0712
MOUNTING HOLES AND JM1 CONNECTOR FOR

MODULE PAGE: 1 OF 3
OVERALL PAGE: 16 OF 99

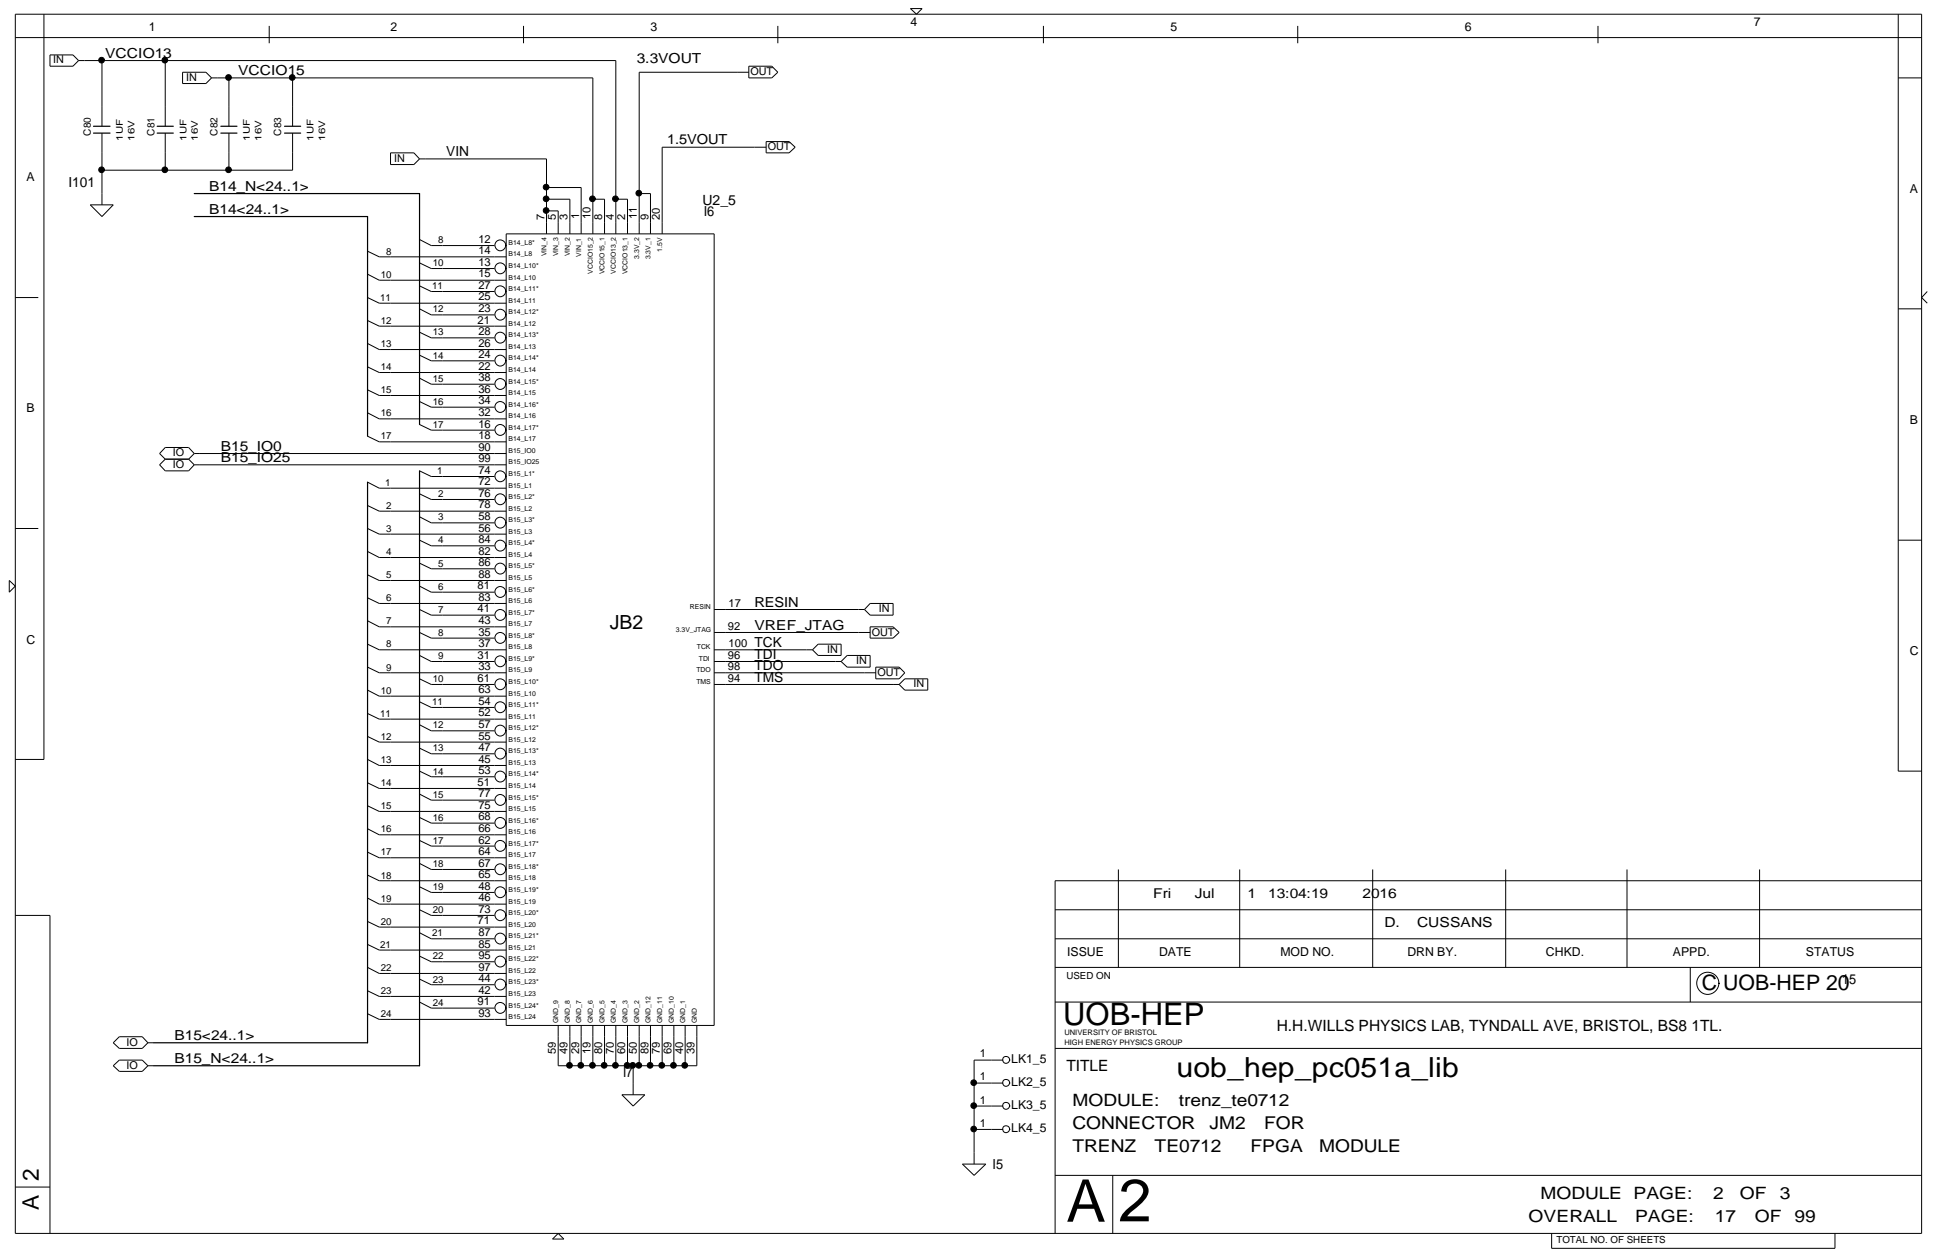
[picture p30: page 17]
TRENZ TE0712; FPGA MODULE; uob_hep_pc051a_lib; TDI; TCK; TMS; TDO; VREF_JTAG; RESIN; 1.5VOUT; VCCIO15; VCCIO13; 3.3VOUT; VIN; 3.3V_JTAG; VIN_4; VIN_3; VIN_2; VIN_1; VCCIO15_2; VCCIO15_1; VCCIO13_2; VCCIO13_1; GND_9; GND_8; GND_7; GND_6; GND_5; GND_4; GND_3; GND_2; GND_12; GND_11; GND_10; GND_1; GND; OUT; UOB-HEP

Fri Jul | 1 13:04:19 2016

D. CUSSANS

ISSUE | DATE | MOD NO. | DRN BY. | CHKD. | APPD. | STATUS
USED ON | C UOB-HEP 20 15

H.H.WILLS PHYSICS LAB, TYNDALL AVE, BRISTOL, BS8 1TL.

UNIVERSITY OF BRISTOL
HIGH ENERGY PHYSICS GROUP
TITLE
MODULE: trenz_te0712
CONNECTOR JM2 FOR

MODULE PAGE: 2 OF 3
OVERALL PAGE: 17 OF 99

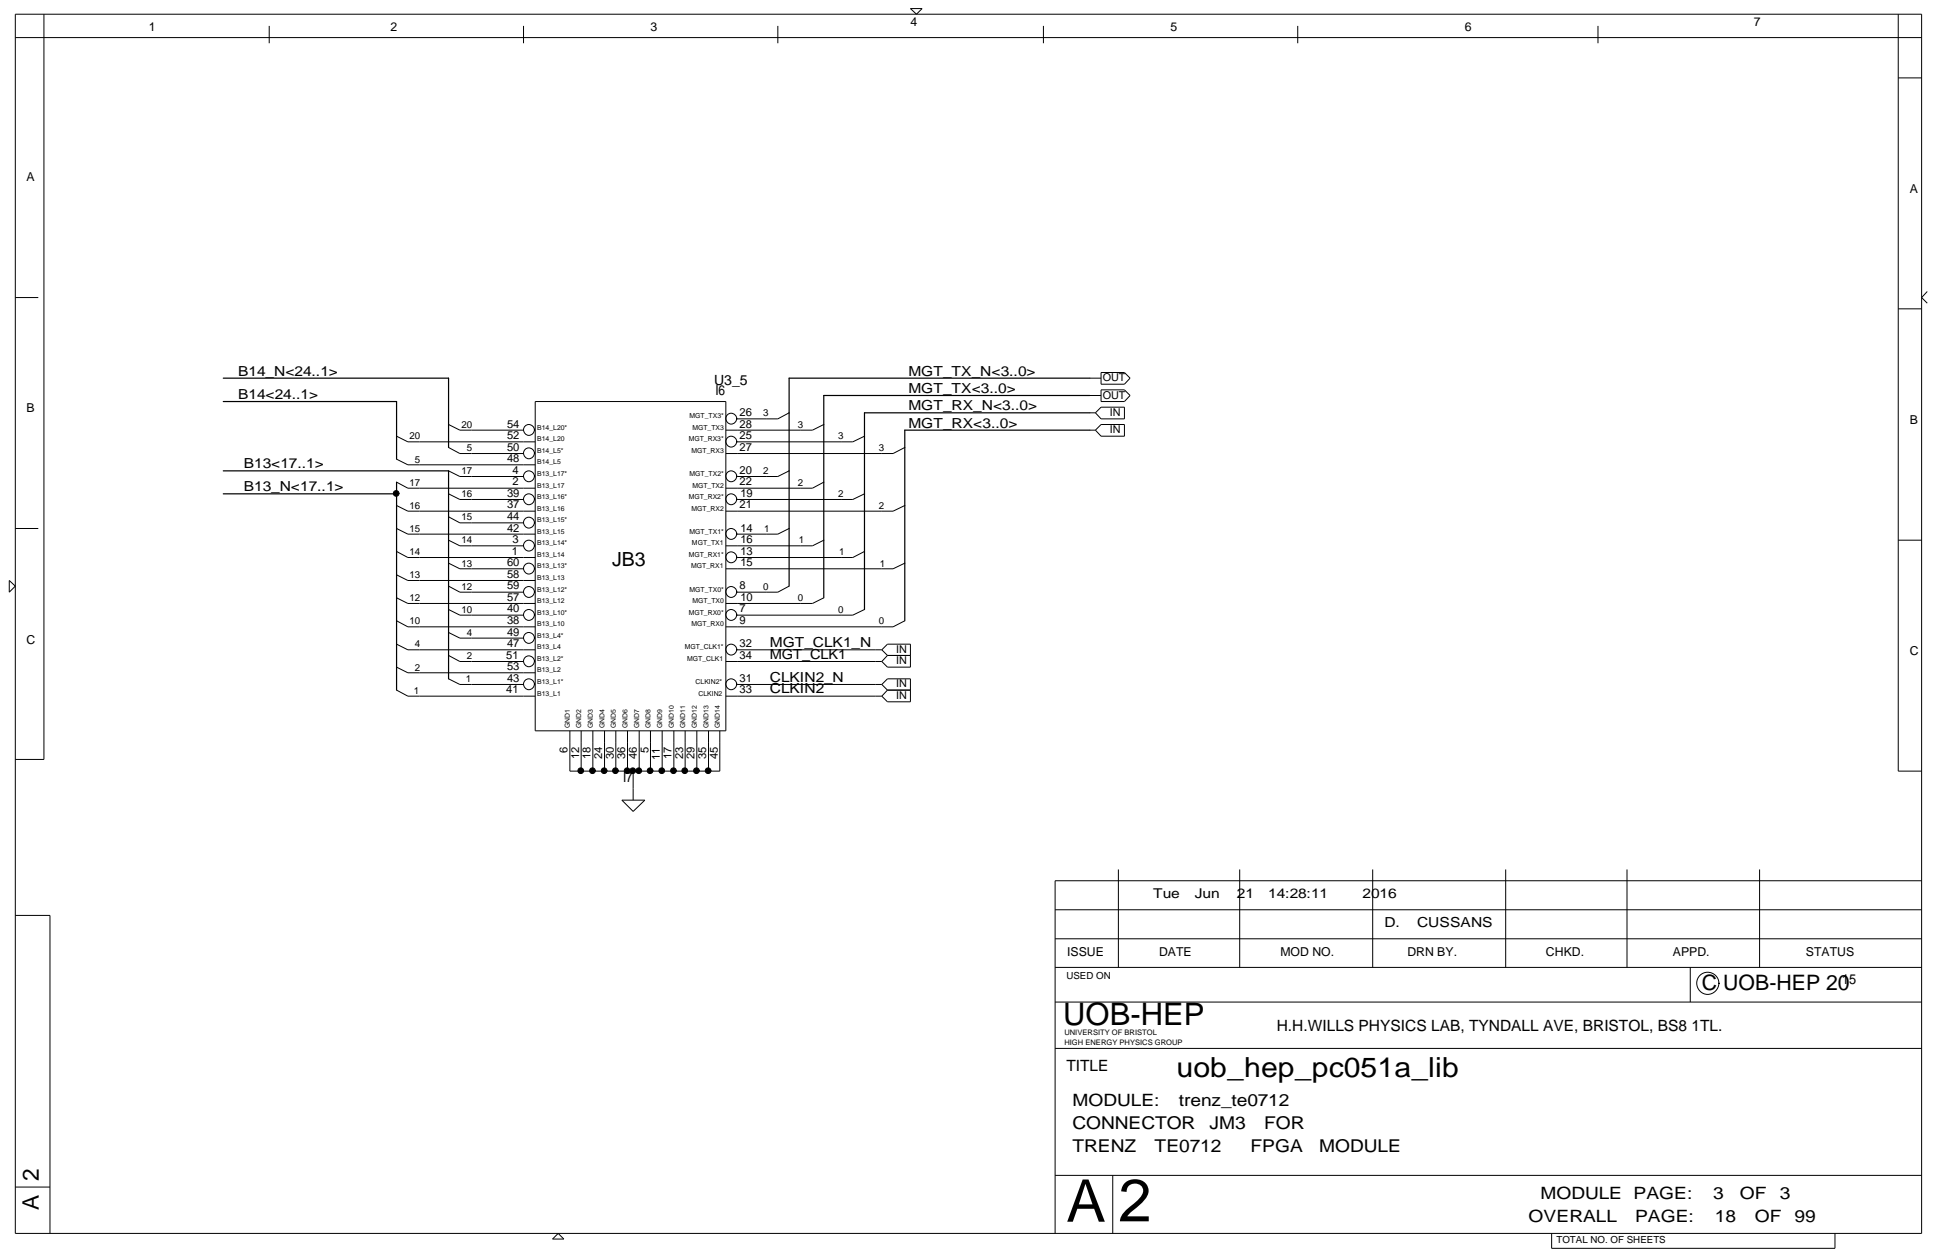
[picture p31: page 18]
TRENZ TE0712; FPGA MODULE; uob_hep_pc051a_lib; MGT_CLK1_N MGT_CLK1; CLKIN2_N CLKIN2; MGT_RX_N<3..0>; MGT_TX_N<3..0> MGT_TX<3..0>; MGT_RX<3..0>; MGT_TX3* MGT_TX3 MGT_RX3* MGT_RX3; MGT_TX2* MGT_TX2 MGT_RX2* MGT_RX2; MGT_TX1* MGT_TX1 MGT_RX1* MGT_RX1; MGT_TX0* MGT_TX0 MGT_RX0* MGT_RX0; MGT_CLK1* MGT_CLK1; CLKIN2* CLKIN2; GND1; GND2; GND3; GND4; GND5; GND6; GND7; GND8; GND9; GND10; GND11; GND12; GND13; GND14; OUT; UOB-HEP

Tue Jun 21 14:28:11 | 2016

D. CUSSANS

ISSUE | DATE | MOD NO. | DRN BY. | CHKD. | APPD. | STATUS
USED ON | C UOB-HEP 20 15

H.H.WILLS PHYSICS LAB, TYNDALL AVE, BRISTOL, BS8 1TL.

UNIVERSITY OF BRISTOL
HIGH ENERGY PHYSICS GROUP
TITLE
MODULE: trenz_te0712
CONNECTOR JM3 FOR

MODULE PAGE: 3 OF 3
OVERALL PAGE: 18 OF 99

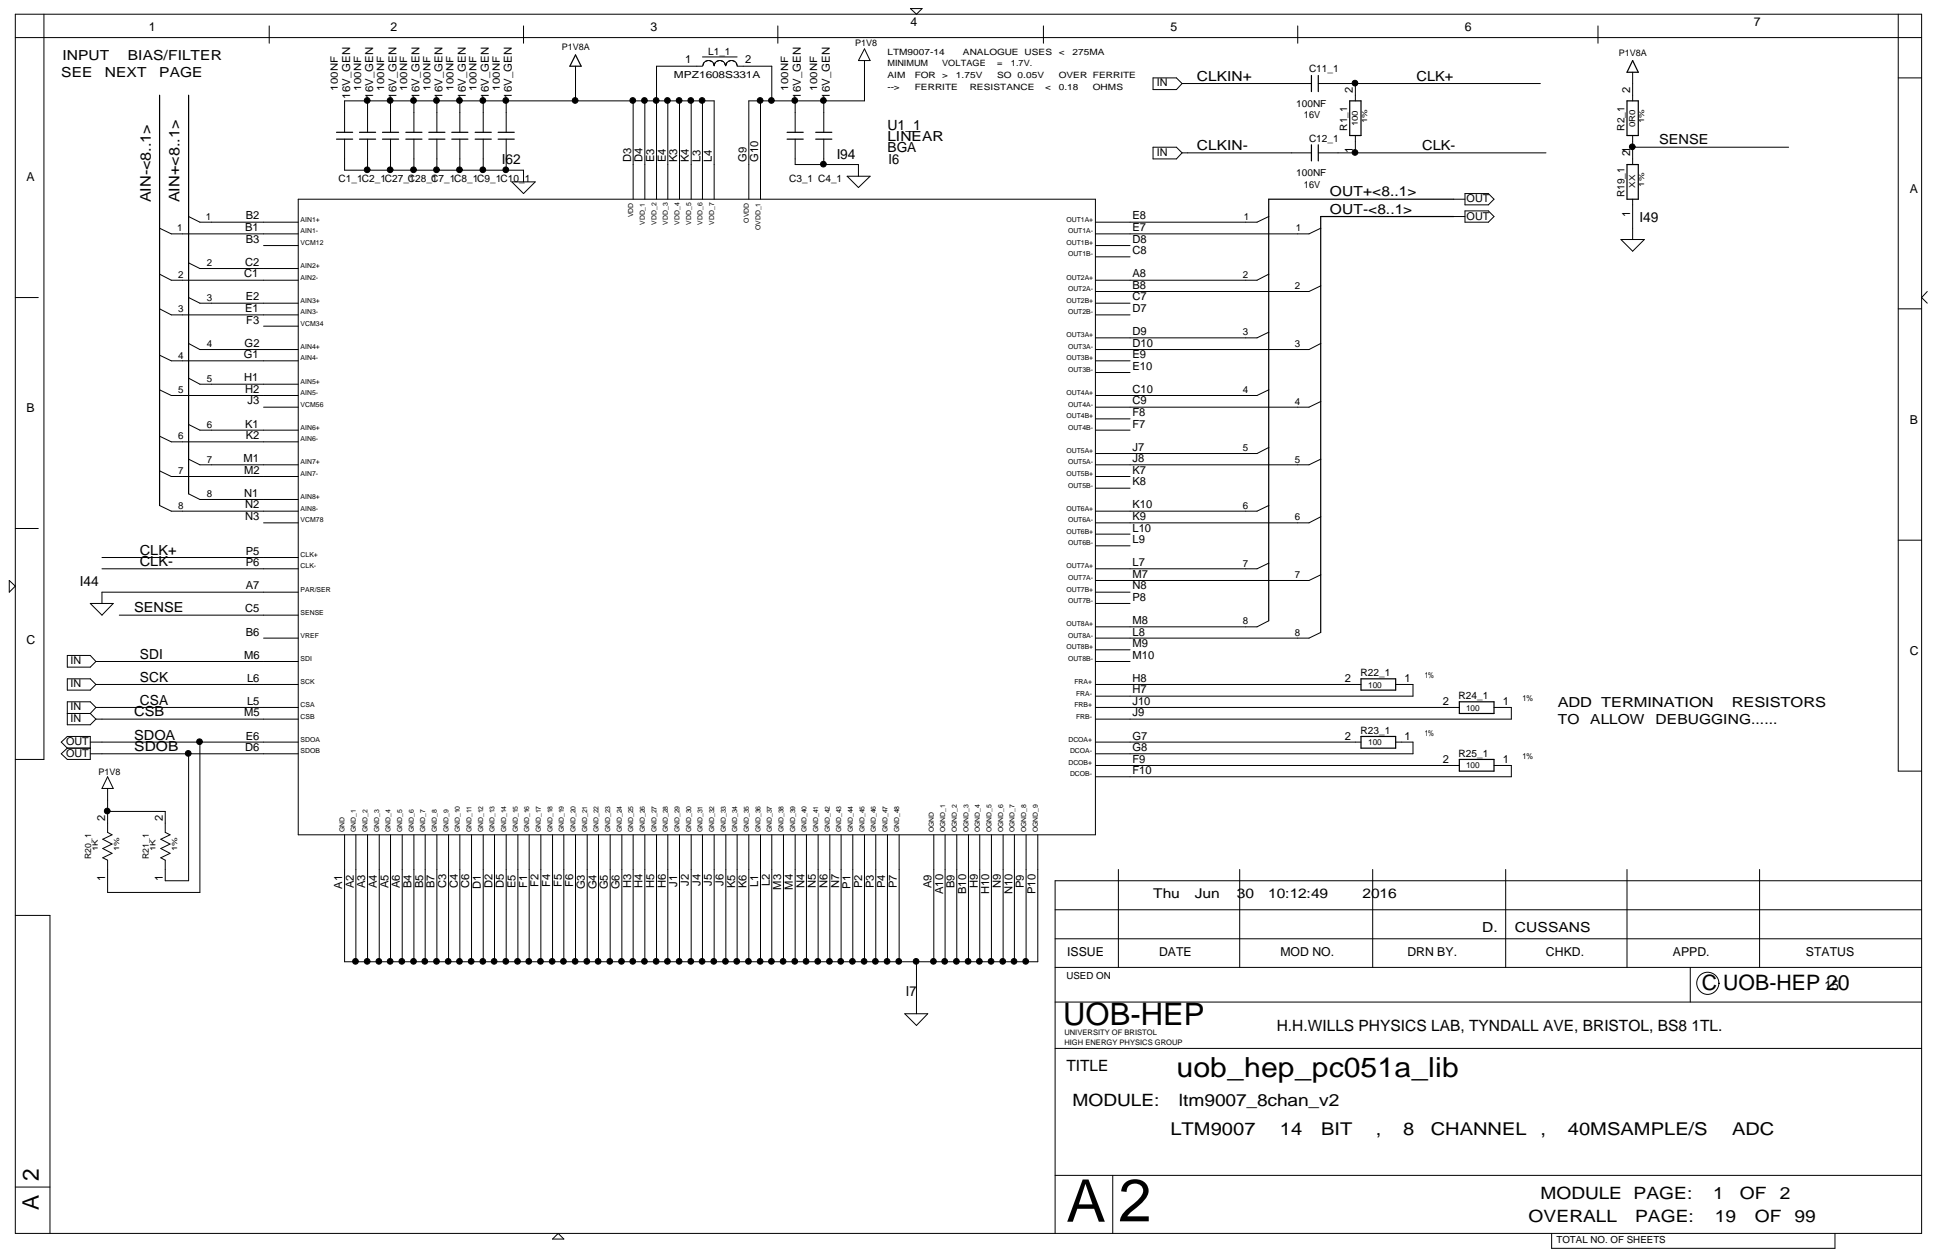
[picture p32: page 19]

Thu Jun 30 10:12:49 | 2016

D. CUSSANS

ISSUE | DATE | MOD NO. | DRN BY. | CHKD. | APPD. | STATUS
USED ON | C UOB-HEP 20 15

H.H.WILLS PHYSICS LAB, TYNDALL AVE, BRISTOL, BS8 1TL.

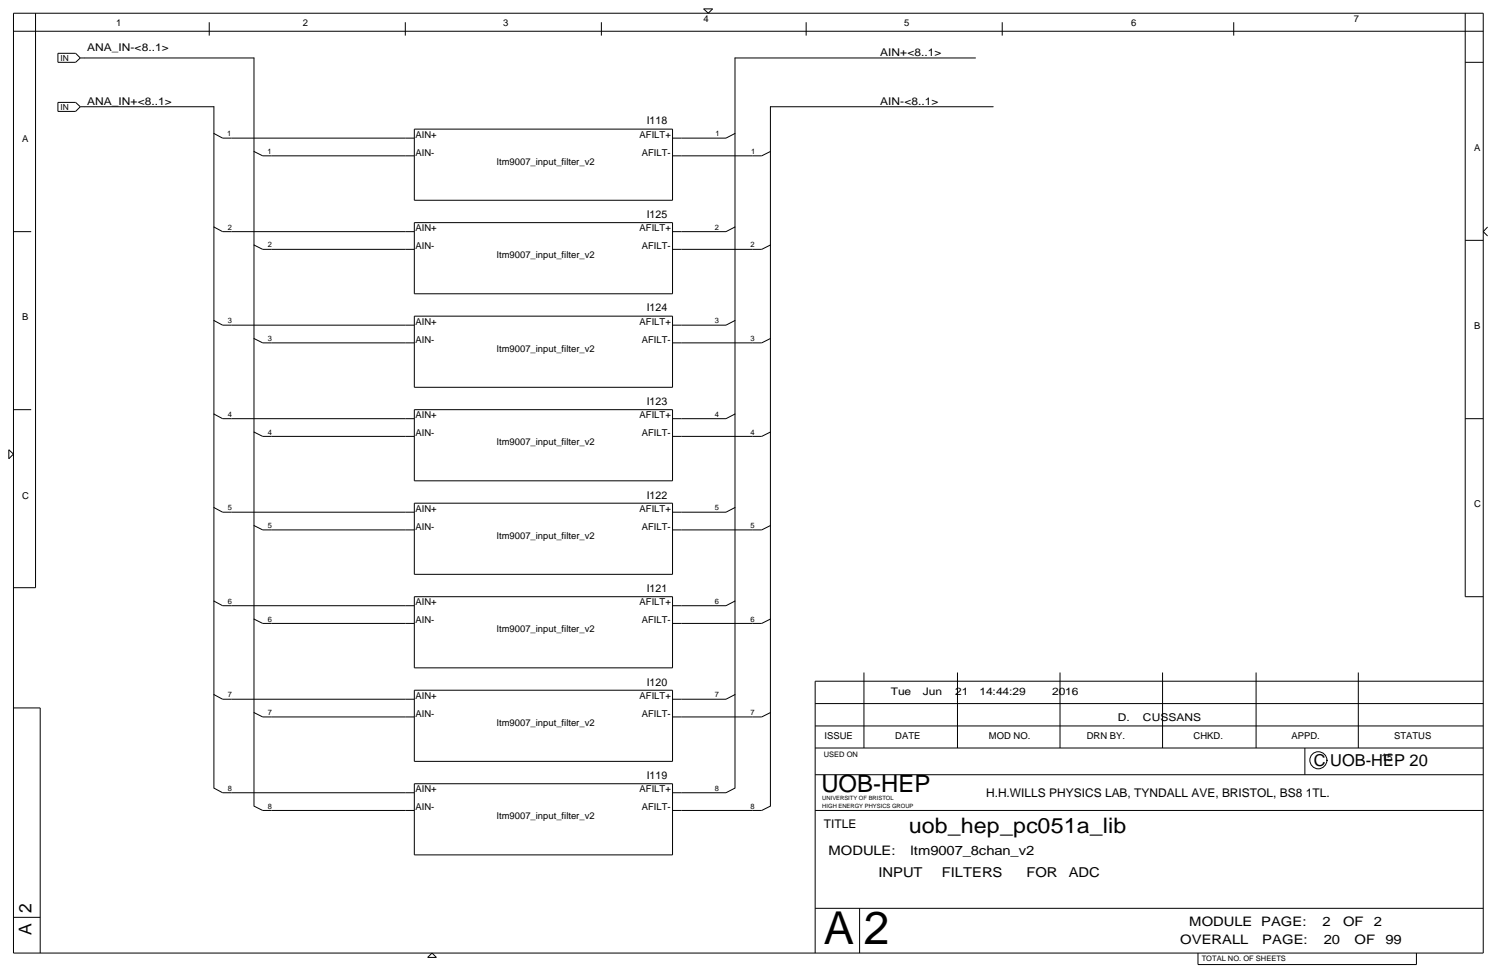
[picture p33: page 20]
INPUT; FILTERS; FOR ADC; uob_hep_pc051a_lib; ANA_IN+<8..1>; AIN+<8..1> ANA_IN-<8..1>; AIN-<8..1>; ltm9007_input_filter_v2; AFILT-; UOB-HEP

AFILT+ AIN- AIN+

Tue Jun 21 14:44:29 | 2016

D. CUSSANS

ISSUE | DATE | MOD NO. | DRN BY. | CHKD. | APPD. | STATUS
USED ON | C UOB-HEP 20 15

H.H.WILLS PHYSICS LAB, TYNDALL AVE, BRISTOL, BS8 1TL.

UNIVERSITY OF BRISTOL
HIGH ENERGY PHYSICS GROUP
TITLE
MODULE: ltm9007_8chan_v2

MODULE PAGE: 2 OF 2
OVERALL PAGE: 20 OF 99

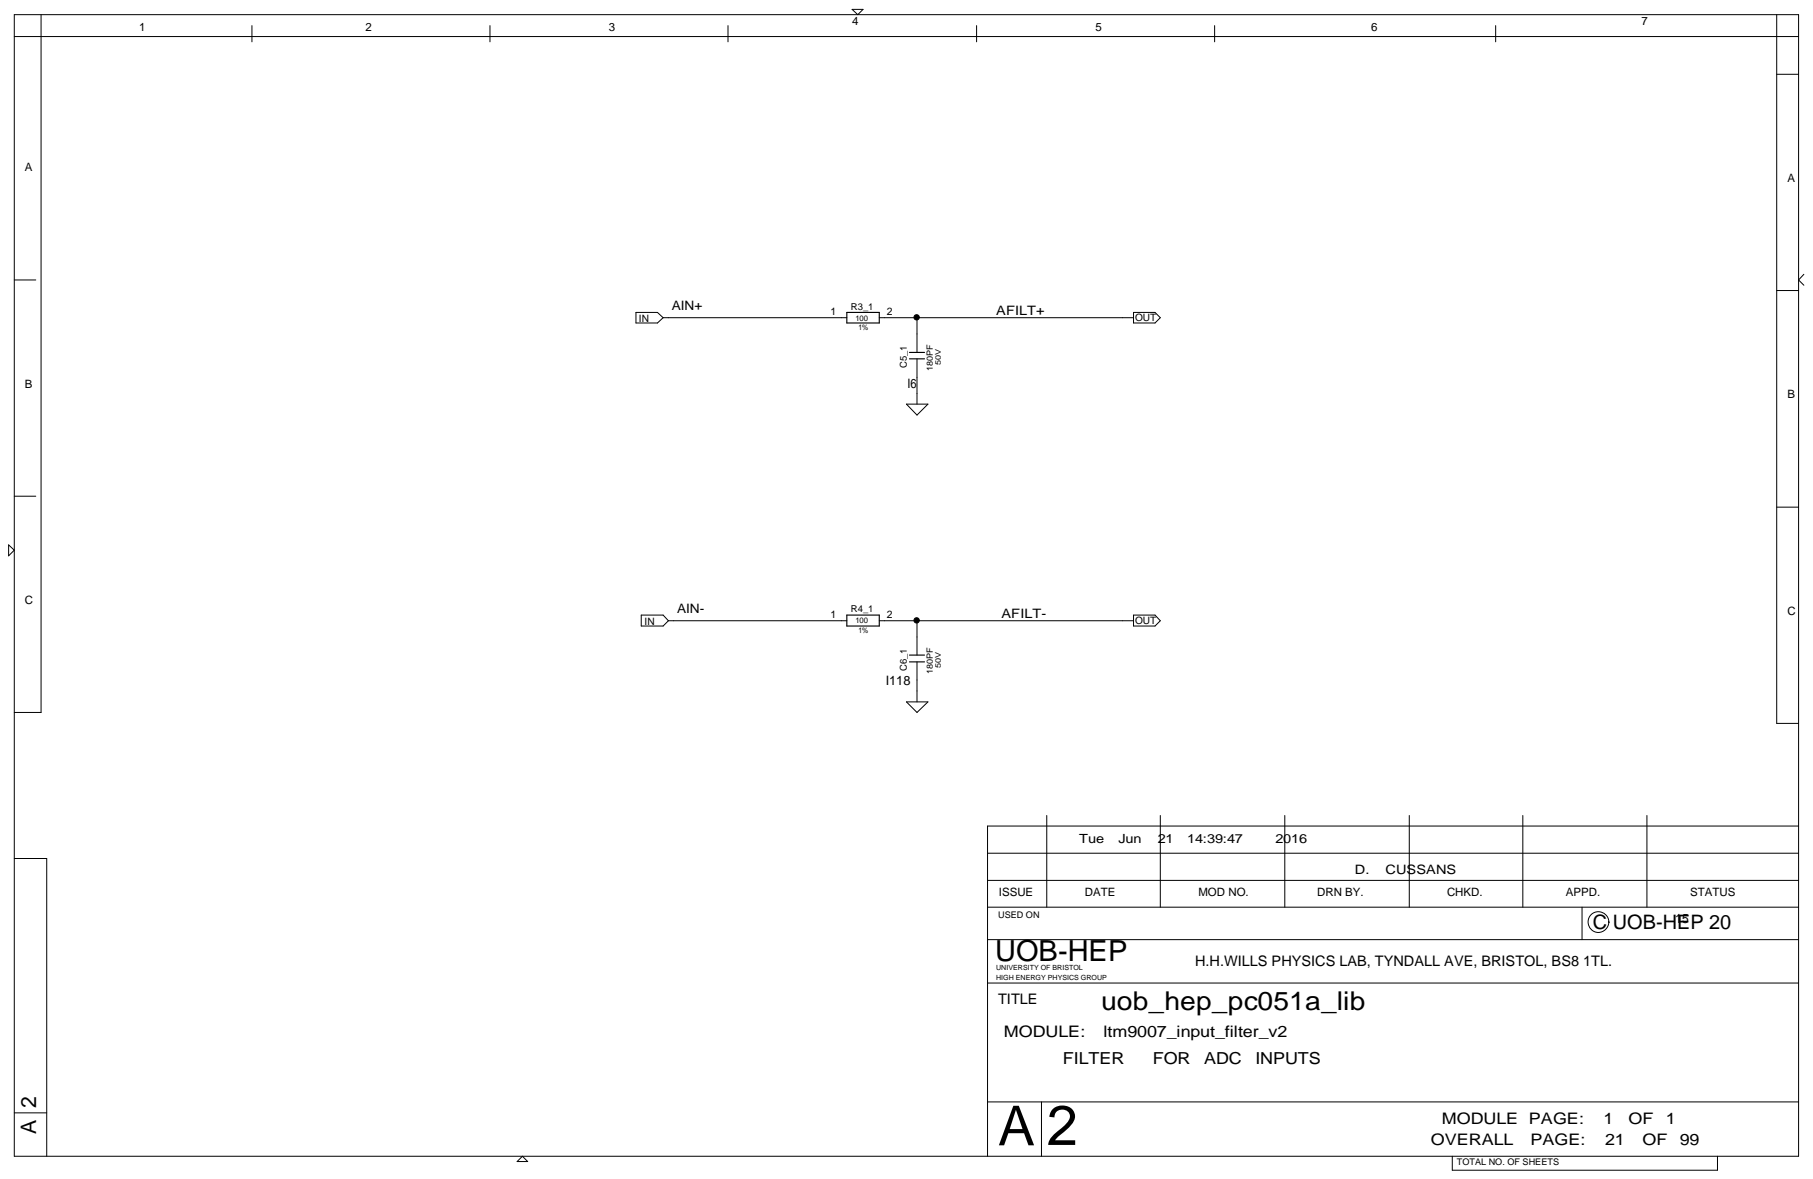
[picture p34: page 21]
FILTER; FOR ADC INPUTS; uob_hep_pc051a_lib; AIN-; AIN+; AFILT- 100; AFILT+; C6_1 C5_1 OUT; OUT; UOB-HEP

Tue Jun 21 14:39:47 | 2016

D. CUSSANS

ISSUE | DATE | MOD NO. | DRN BY. | CHKD. | APPD. | STATUS
USED ON | C UOB-HEP 20 15

H.H.WILLS PHYSICS LAB, TYNDALL AVE, BRISTOL, BS8 1TL.

UNIVERSITY OF BRISTOL
HIGH ENERGY PHYSICS GROUP
TITLE
MODULE: ltm9007_input_filter_v2

MODULE PAGE: 1 OF 1
OVERALL PAGE: 21 OF 99

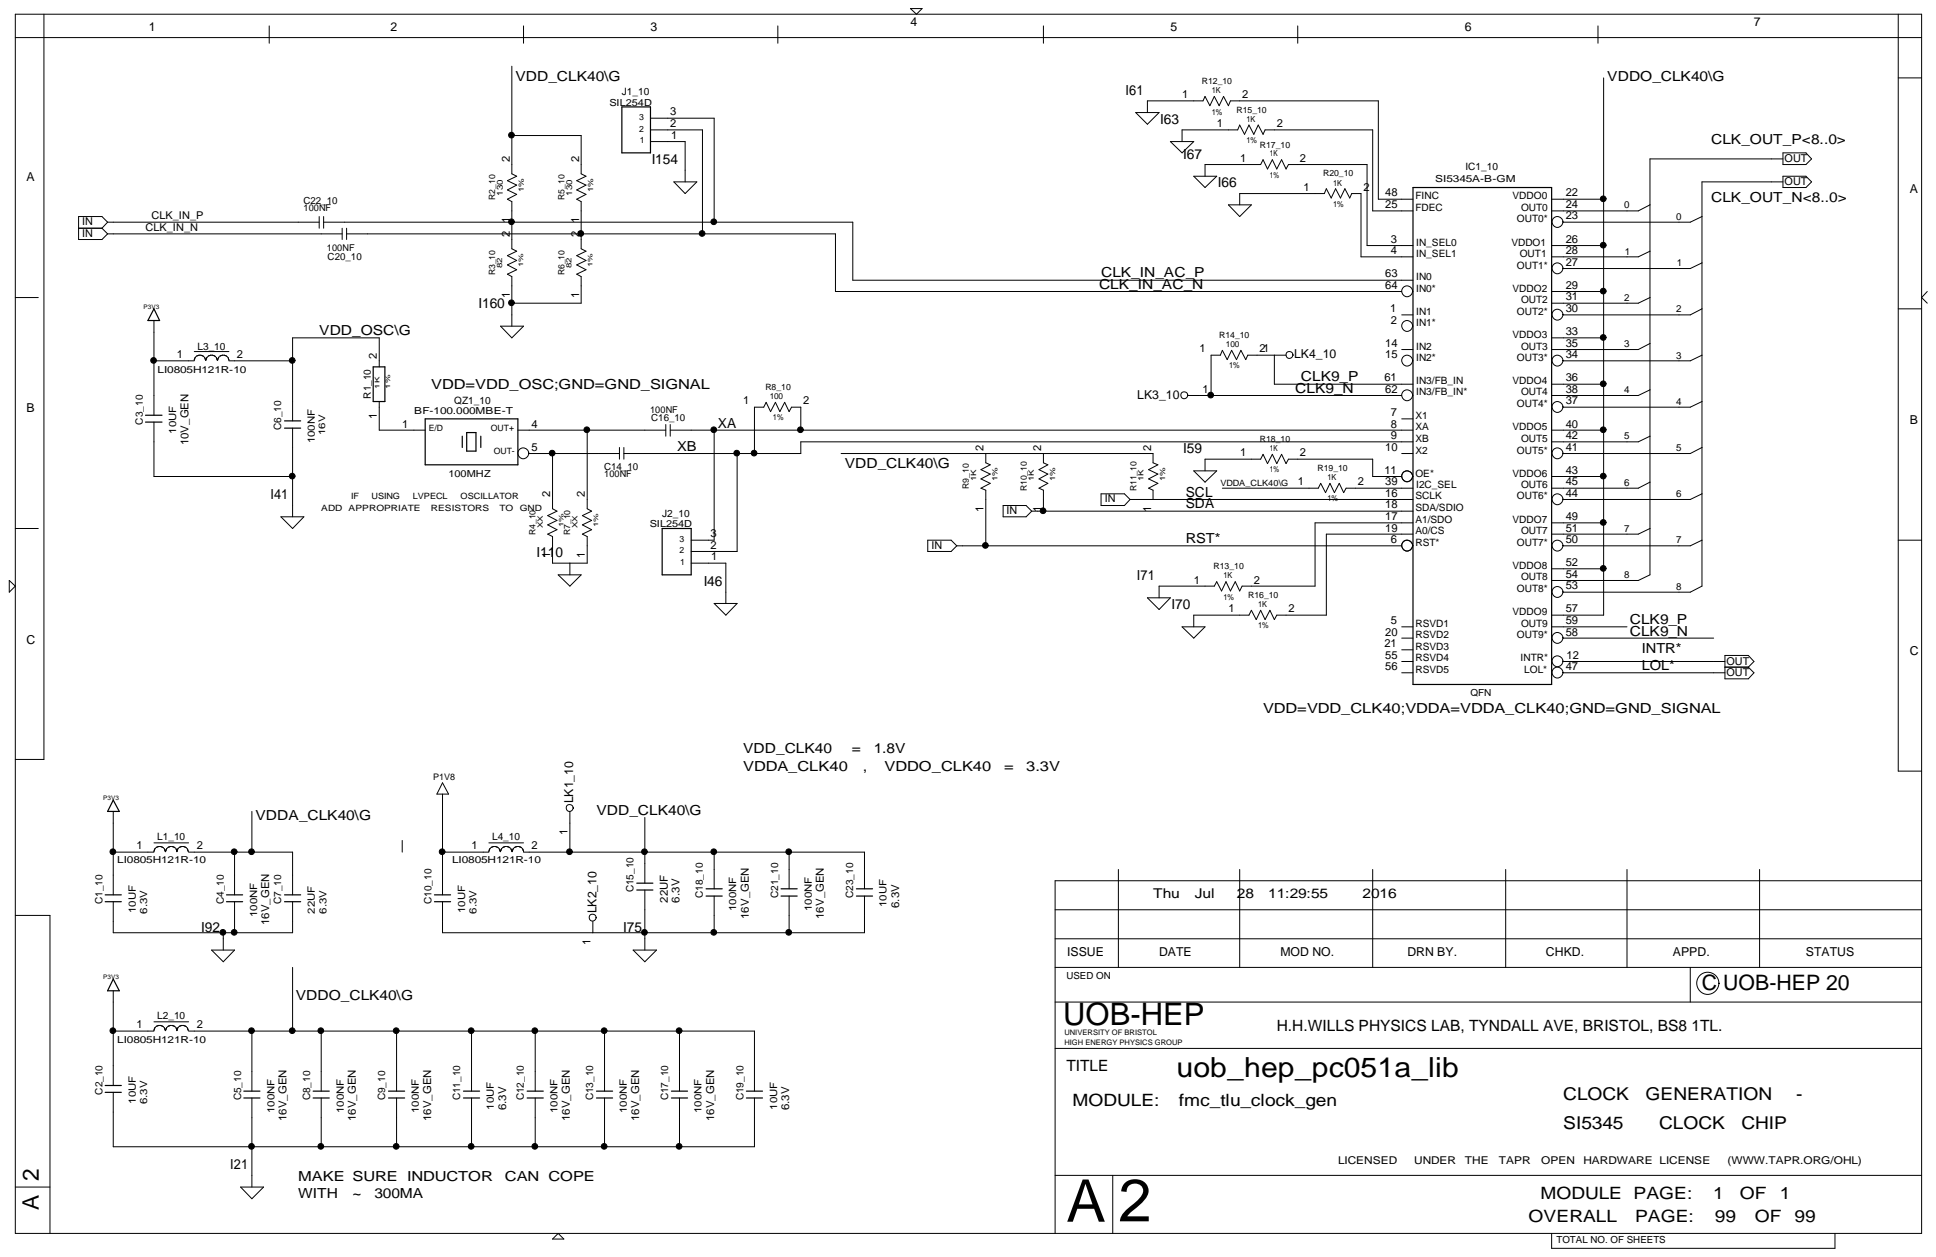
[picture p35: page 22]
VDD_CLK40; USING; LVPECL; OSCILLATOR; LICENSED; UNDER THE TAPR OPEN HARDWARE LICENSE; (WWW.TAPR.ORG/OHL); CLOCK GENERATION -; CLOCK CHIP; VDDA_CLK40 , VDDO_CLK40 = 3.3V; Thu Jul; uob_hep_pc051a_lib; VDDA_CLK40\G; VDD=VDD_OSC;GND=GND_SIGNAL; BF-100.000MBE-T; VDDO_CLK40\G; VDD_CLK40\G; VDD_OSC\G; SIL254D; CLK9_N; CLK9_P; CLK9_N CLK9_P; RST*; SCL SDA; QFN; CLK_OUT_N<8..0>; CLK_OUT_P<8..0>; 16V_GEN 100NF; 16V_GEN; 100MHZ; 10V_GEN 10UF; INTR*; CLK_IN_AC_P CLK_IN_AC_N; CLK_IN_P CLK_IN_N; LOL*; OUT-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

ADD APPROPRIATE RESISTORS TO GND

VDD=VDD_CLK40;VDDA=VDDA_CLK40;GND=GND_SIGNAL

ISSUE | DATE | MOD NO. | DRN BY. | CHKD. | APPD. | STATUS

USED ON | C UOB-HEP 20

H.H.WILLS PHYSICS LAB, TYNDALL AVE, BRISTOL, BS8 1TL.

UNIVERSITY OF BRISTOL
HIGH ENERGY PHYSICS GROUP
TITLE
MODULE: fmc_tlu_clock_gen

MAKE SURE INDUCTOR CAN COPE
WITH ~ 300MA

MODULE PAGE: 1 OF 1
OVERALL PAGE: 99 OF 99

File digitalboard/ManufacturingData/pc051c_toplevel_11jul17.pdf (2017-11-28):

## 8 X LTM9007

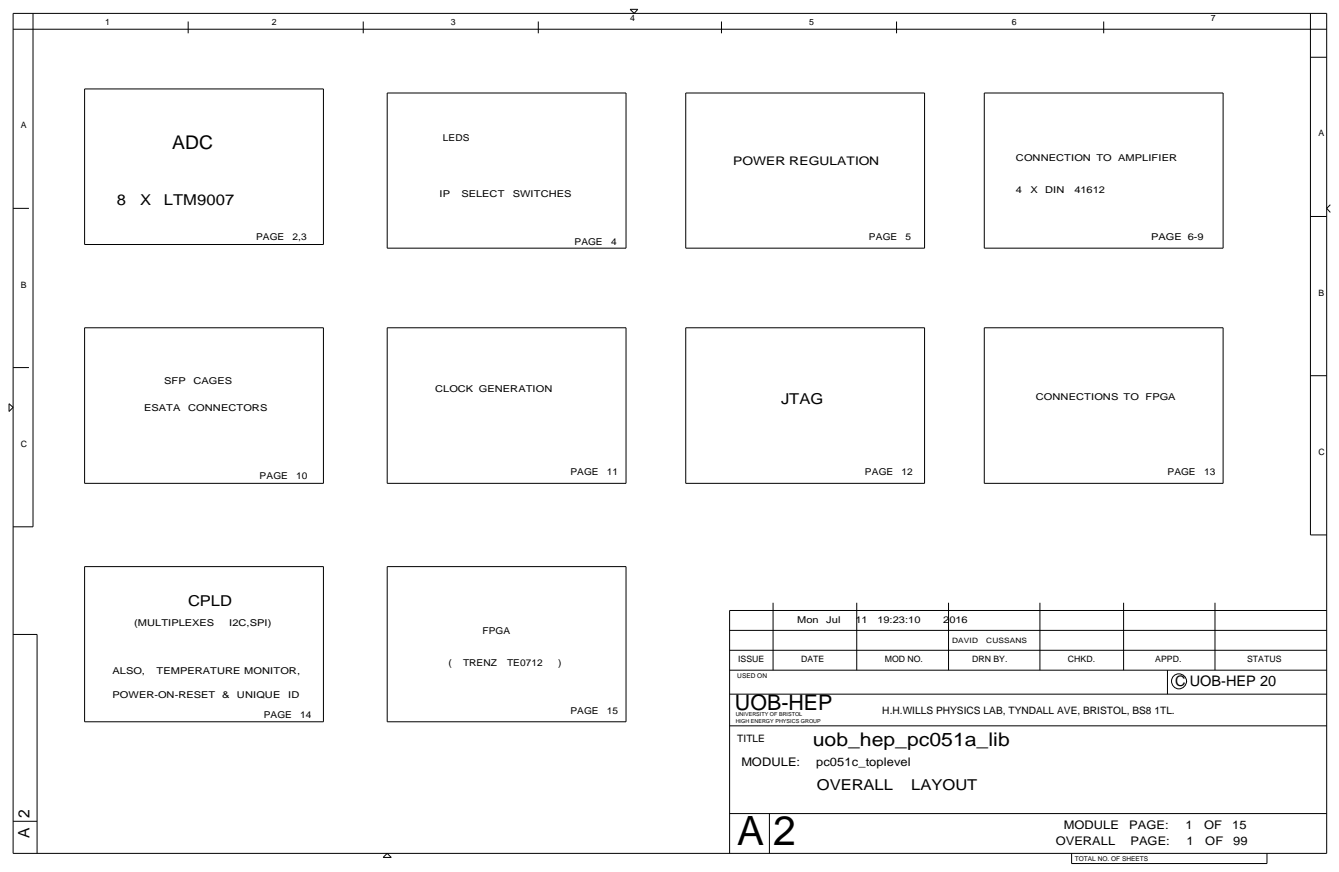
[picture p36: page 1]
PAGE 15; FPGA; ( TRENZ TE0712; PAGE 14; PAGE 13; JTAG; PAGE 12 PAGE 10; SFP CAGES; 4 X DIN 41612; PAGE 5; PAGE 6-9 PAGE 4 PAGE 2,3; POWER REGULATION; LEDS ADC; OVERALL LAYOUT; PAGE 11; CLOCK GENERATION; ESATA CONNECTORS; CPLD; (MULTIPLEXES; I2C,SPI); OVERALL PAGE:; MODULE PAGE:; uob_hep_pc051a_lib; UOB-HEP

CONNECTION TO AMPLIFIER

IP SELECT SWITCHES

CONNECTIONS TO FPGA

Mon Jul | 11 19:23:10 2016

DAVID CUSSANS

ISSUE | DATE | MOD NO. | DRN BY. | CHKD. | APPD. | STATUS

ALSO, TEMPERATURE MONITOR,

USED ON | C UOB-HEP 20

POWER-ON-RESET & UNIQUE ID

UNIVERSITY OF BRISTOL
HIGH ENERGY PHYSICS GROUP
TITLE
MODULE: pc051c_toplevel

H.H.WILLS PHYSICS LAB, TYNDALL AVE, BRISTOL, BS8 1TL.

TOTAL NO. OF SHEETS

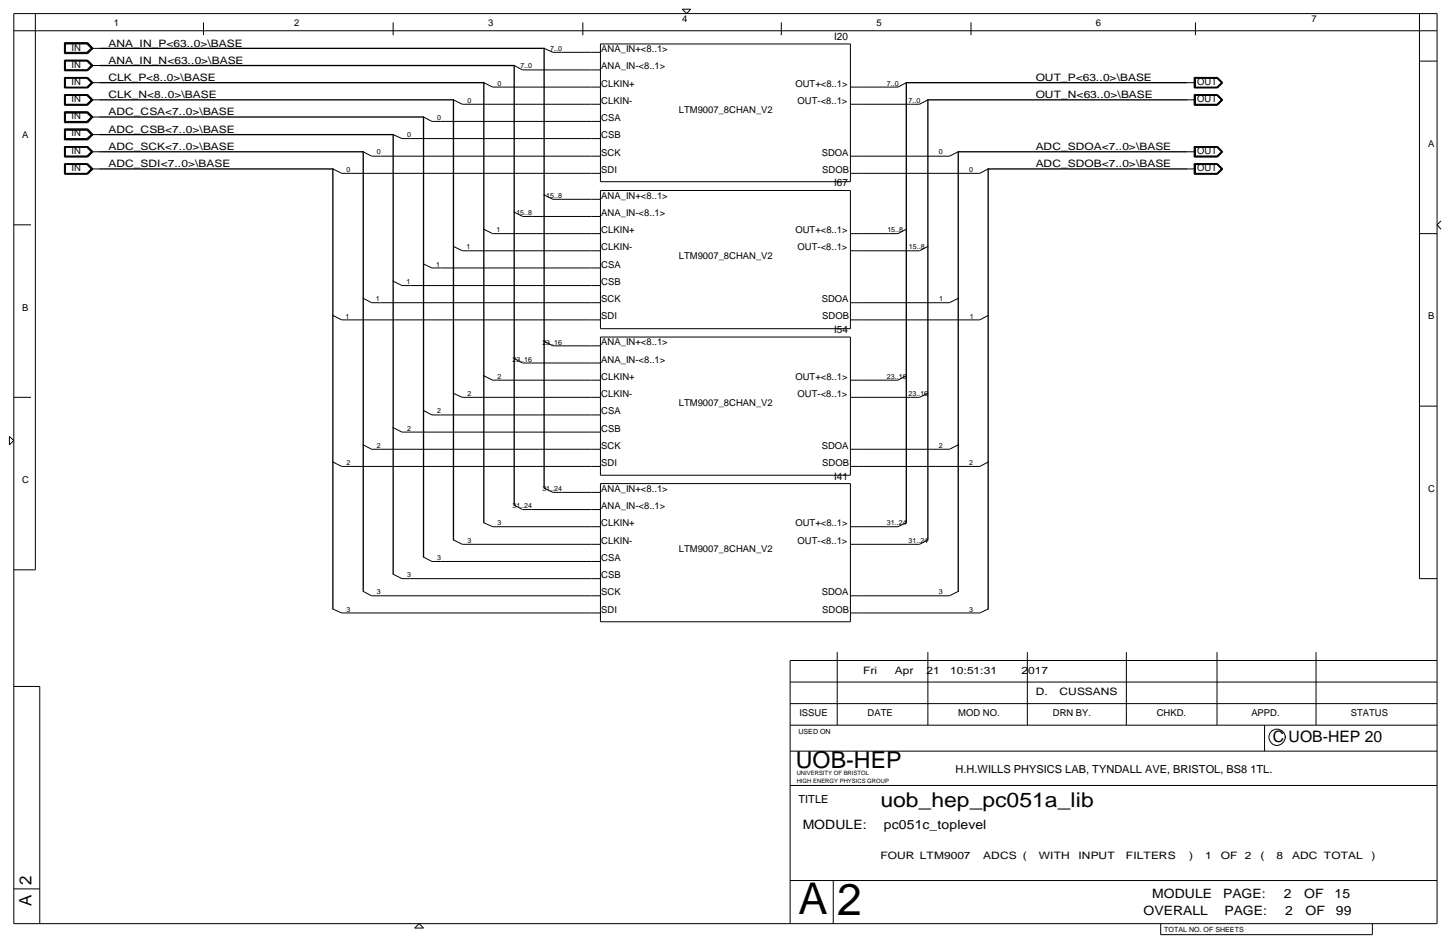
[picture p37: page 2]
OVERALL PAGE:; MODULE PAGE:; uob_hep_pc051a_lib; CLK_N<8..0>\BASE; CLK_P<8..0>\BASE; OUT_P<63..0>\BASE; OUT_N<63..0>\BASE; ADC_SDI<7..0>\BASE; ADC_SDOB<7..0>\BASE; ADC_CSB<7..0>\BASE; ADC_CSA<7..0>\BASE; ANA_IN_P<63..0>\BASE ANA_IN_N<63..0>\BASE; ADC_SCK<7..0>\BASE; ADC_SDOA<7..0>\BASE; LTM9007_8CHAN_V2; ANA_IN+<8..1>; CLKIN+; ANA_IN-<8..1>; CLKIN-; CSA; CSB; SCK; SDI; SDOB; SDOA; OUT-<8..1>; OUT+<8..1>; OUT; UOB-HEP

Fri Apr 21 10:51:31 | 2017

D. CUSSANS

ISSUE | DATE | MOD NO. | DRN BY. | CHKD. | APPD. | STATUS

USED ON | C UOB-HEP 20

UNIVERSITY OF BRISTOL
HIGH ENERGY PHYSICS GROUP
TITLE
MODULE: pc051c_toplevel

H.H.WILLS PHYSICS LAB, TYNDALL AVE, BRISTOL, BS8 1TL.

FOUR LTM9007 ADCS ( WITH INPUT FILTERS ) 1 OF 2 ( 8 ADC TOTAL )

TOTAL NO. OF SHEETS

Fri Apr 21 10:51:31 | 2017

D. CUSSANS

ISSUE | DATE | MOD NO. | DRN BY. | CHKD. | APPD. | STATUS

USED ON | C UOB-HEP 20

UNIVERSITY OF BRISTOL
HIGH ENERGY PHYSICS GROUP
TITLE
MODULE: pc051c_toplevel

H.H.WILLS PHYSICS LAB, TYNDALL AVE, BRISTOL, BS8 1TL.

FOUR LTM9007 ADCS ( WITH INPUT FILTERS ) 2 OF 2 ( 8 ADC TOTAL )

TOTAL NO. OF SHEETS

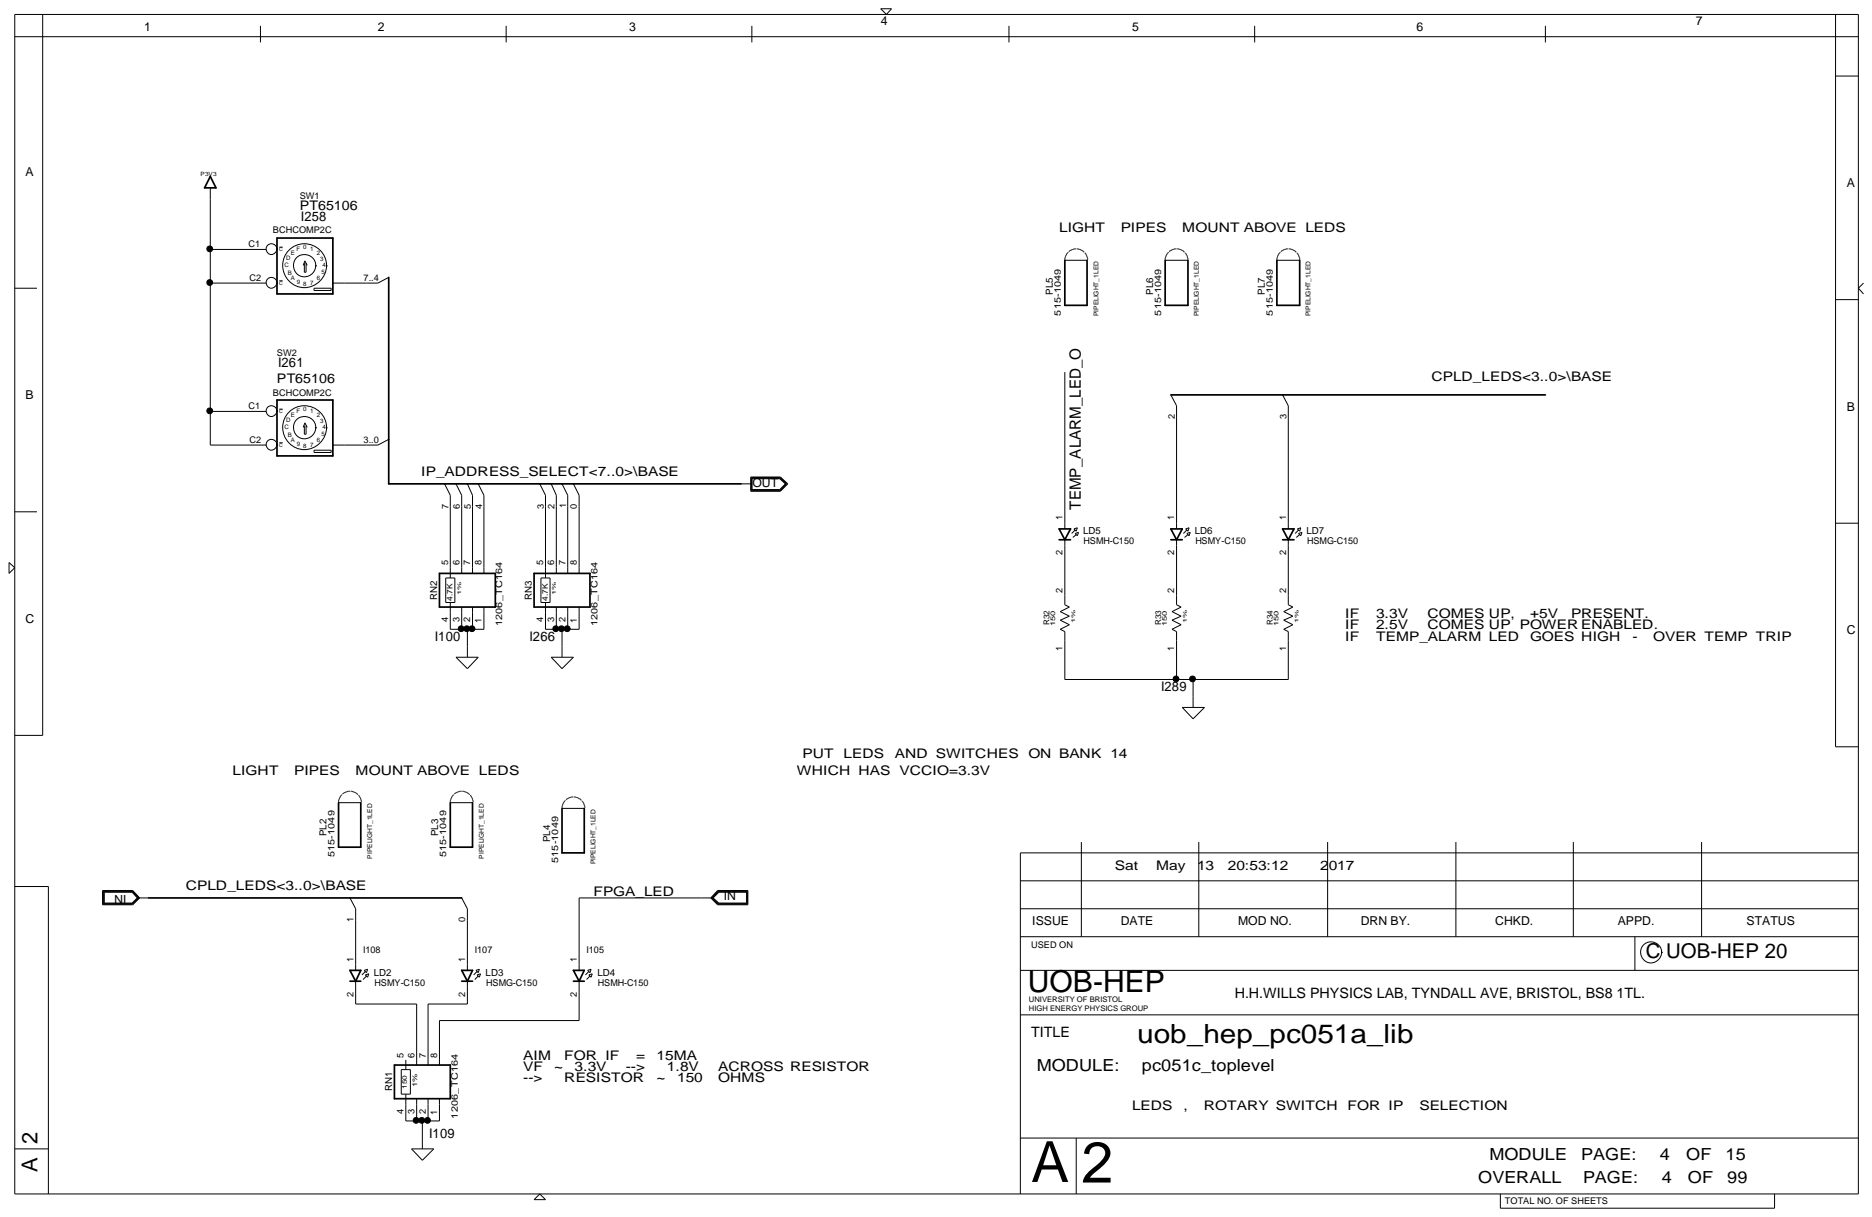
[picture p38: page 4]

LIGHT PIPES MOUNT ABOVE LEDS

IF TEMP_ALARM LED GOES HIGH - OVER TEMP TRIP

PUT LEDS AND SWITCHES ON BANK 14
WHICH HAS VCCIO=3.3V

ISSUE | DATE | MOD NO. | DRN BY. | CHKD. | APPD. | STATUS

USED ON | C UOB-HEP 20

H.H.WILLS PHYSICS LAB, TYNDALL AVE, BRISTOL, BS8 1TL.

LEDS , ROTARY SWITCH FOR IP SELECTION

TOTAL NO. OF SHEETS

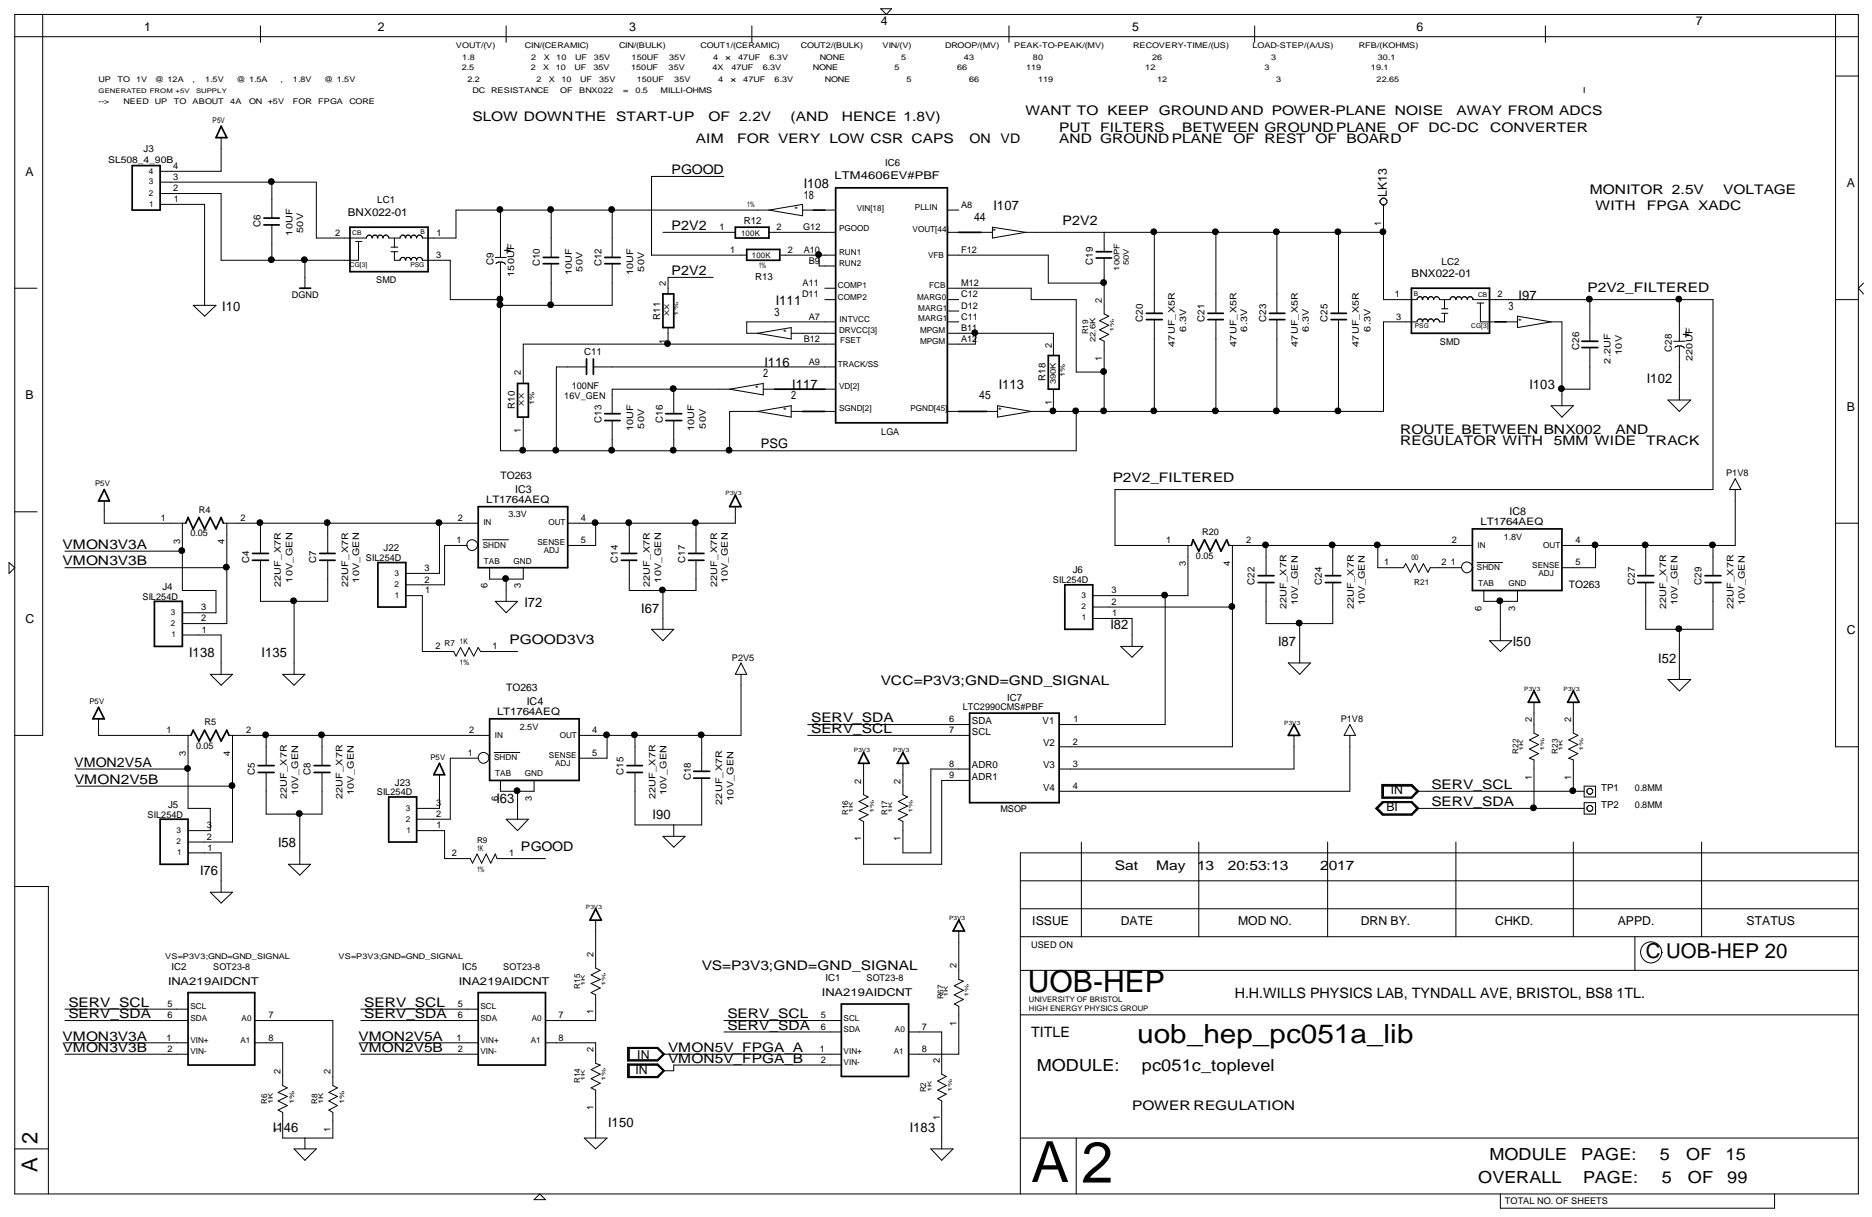
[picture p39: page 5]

WANT TO KEEP GROUND AND POWER-PLANE NOISE AWAY FROM ADCS
PUT FILTERS BETWEEN GROUND PLANE OF DC-DC CONVERTER
AND GROUND PLANE OF REST OF BOARD

AIM FOR VERY LOW CSR CAPS

ROUTE BETWEEN BNX002 AND
REGULATOR WITH 5MM WIDE TRACK

ISSUE | DATE | MOD NO. | DRN BY. | CHKD. | APPD. | STATUS

USED ON | C UOB-HEP 20

UNIVERSITY OF BRISTOL
HIGH ENERGY PHYSICS GROUP
TITLE
MODULE: pc051c_toplevel

H.H.WILLS PHYSICS LAB, TYNDALL AVE, BRISTOL, BS8 1TL.

TOTAL NO. OF SHEETS

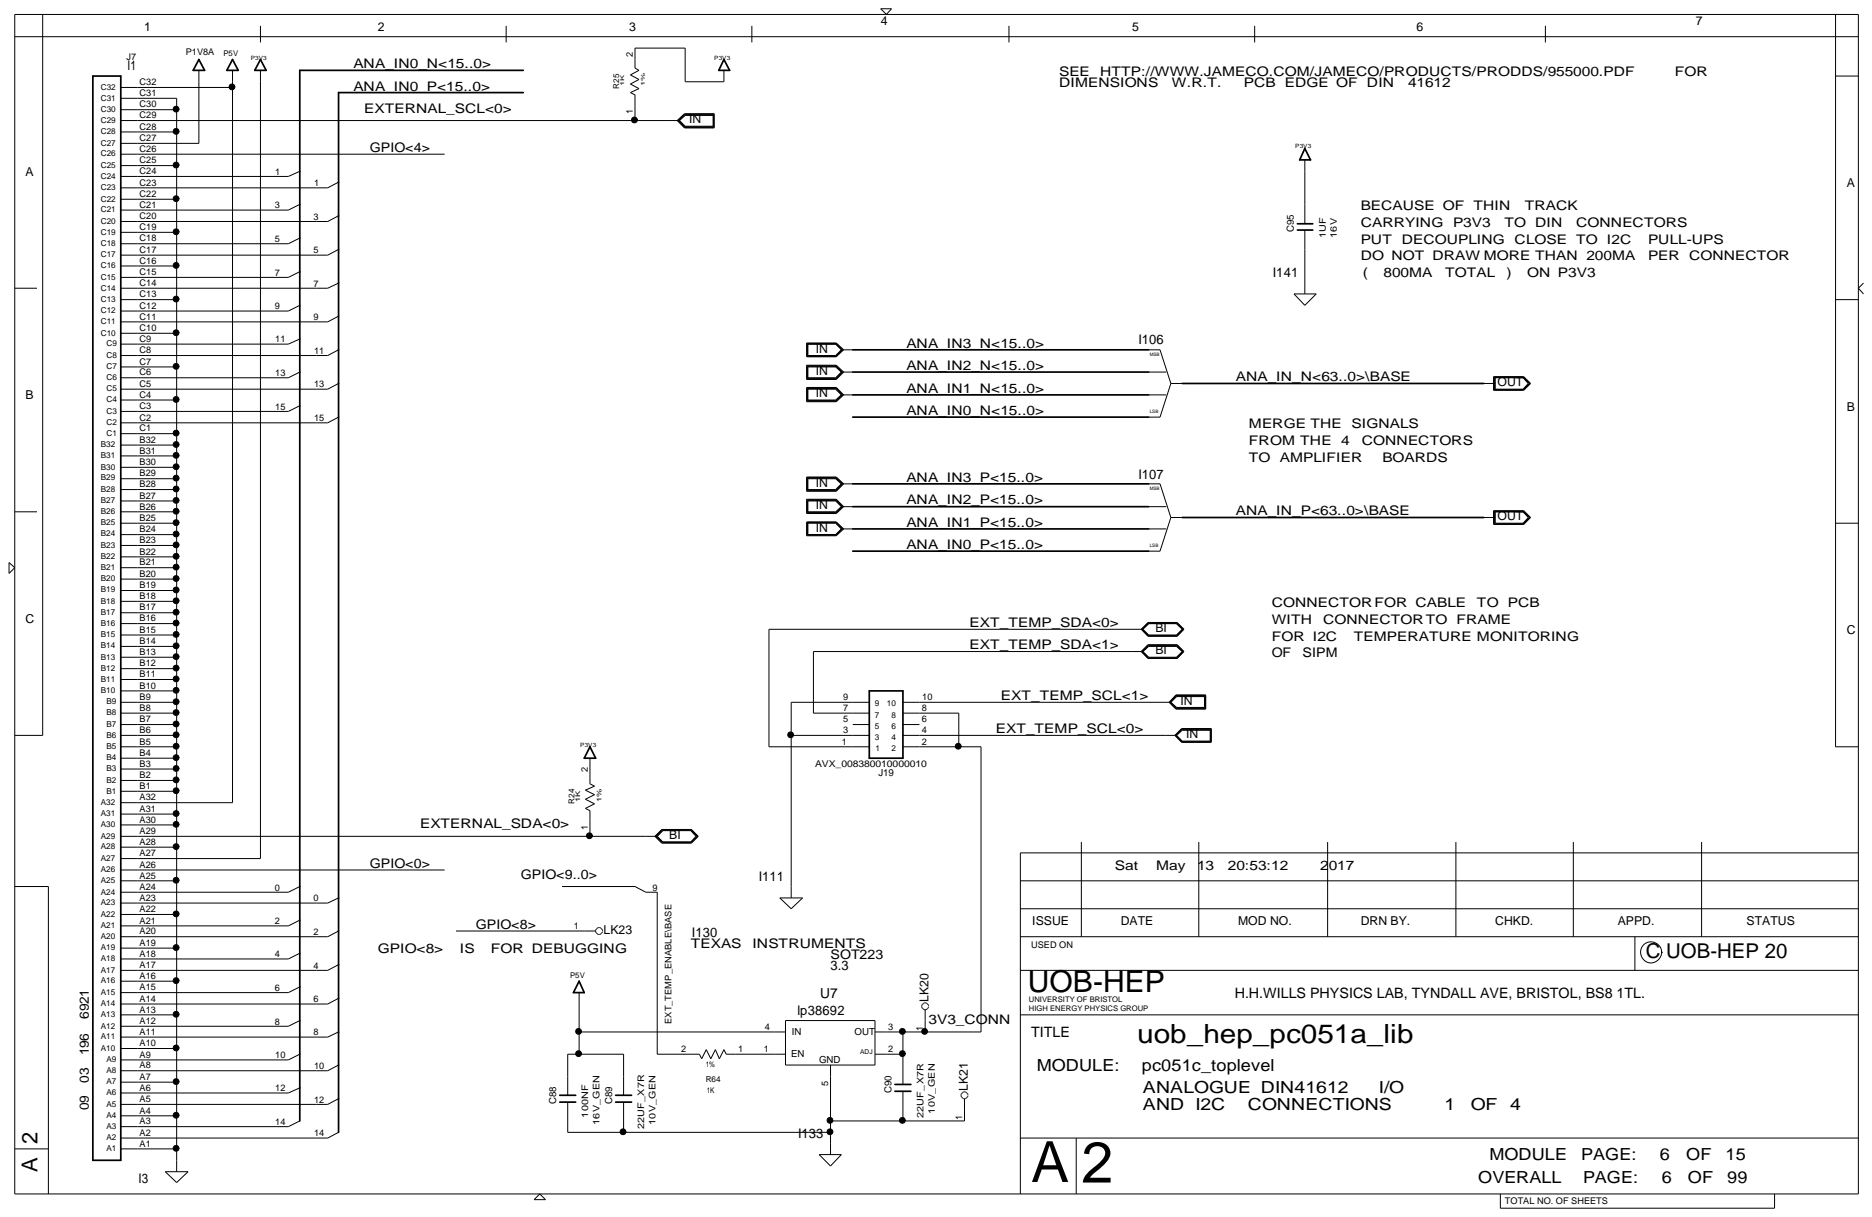
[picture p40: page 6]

BECAUSE OF THIN TRACK
CARRYING P3V3 TO DIN CONNECTORS
PUT DECOUPLING CLOSE TO I2C PULL-UPS
DO NOT DRAW MORE THAN 200MA PER CONNECTOR
( 800MA TOTAL ) ON P3V3

CONNECTORFOR CABLE TO PCB
WITH CONNECTORTO FRAME
FOR I2C TEMPERATURE MONITORING
OF SIPM

GPIO<8> IS FOR DEBUGGING

H.H.WILLS PHYSICS LAB, TYNDALL AVE, BRISTOL, BS8 1TL.

TOTAL NO. OF SHEETS

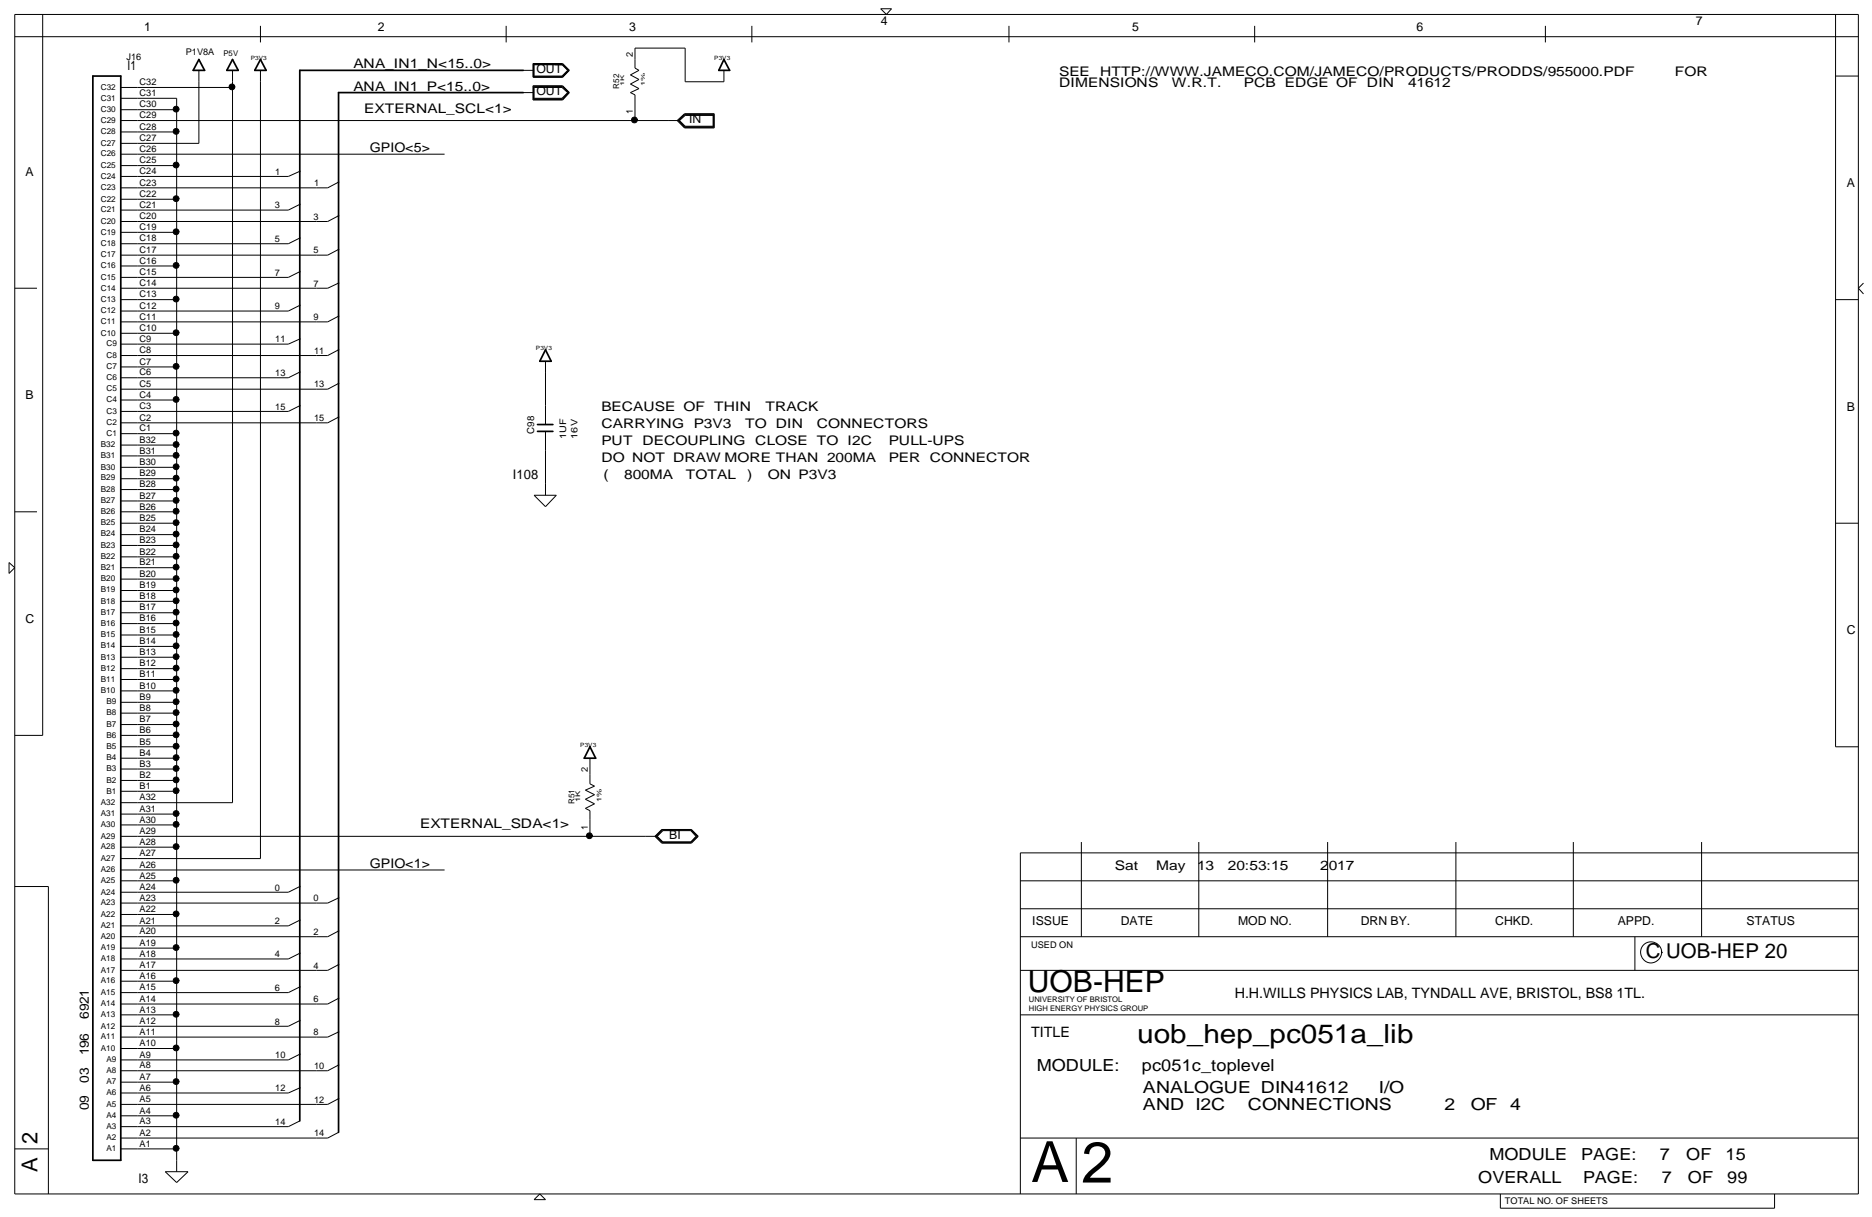
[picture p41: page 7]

BECAUSE OF THIN TRACK
CARRYING P3V3 TO DIN CONNECTORS
PUT DECOUPLING CLOSE TO I2C PULL-UPS
DO NOT DRAW MORE THAN 200MA PER CONNECTOR
( 800MA TOTAL ) ON P3V3

ISSUE | DATE | MOD NO. | DRN BY. | CHKD. | APPD. | STATUS

USED ON | C UOB-HEP 20

09 03 196 6921UNIVERSITY OF BRISTOL HIGH ENERGY PHYSICS GROUP

H.H.WILLS PHYSICS LAB, TYNDALL AVE, BRISTOL, BS8 1TL.

TOTAL NO. OF SHEETS

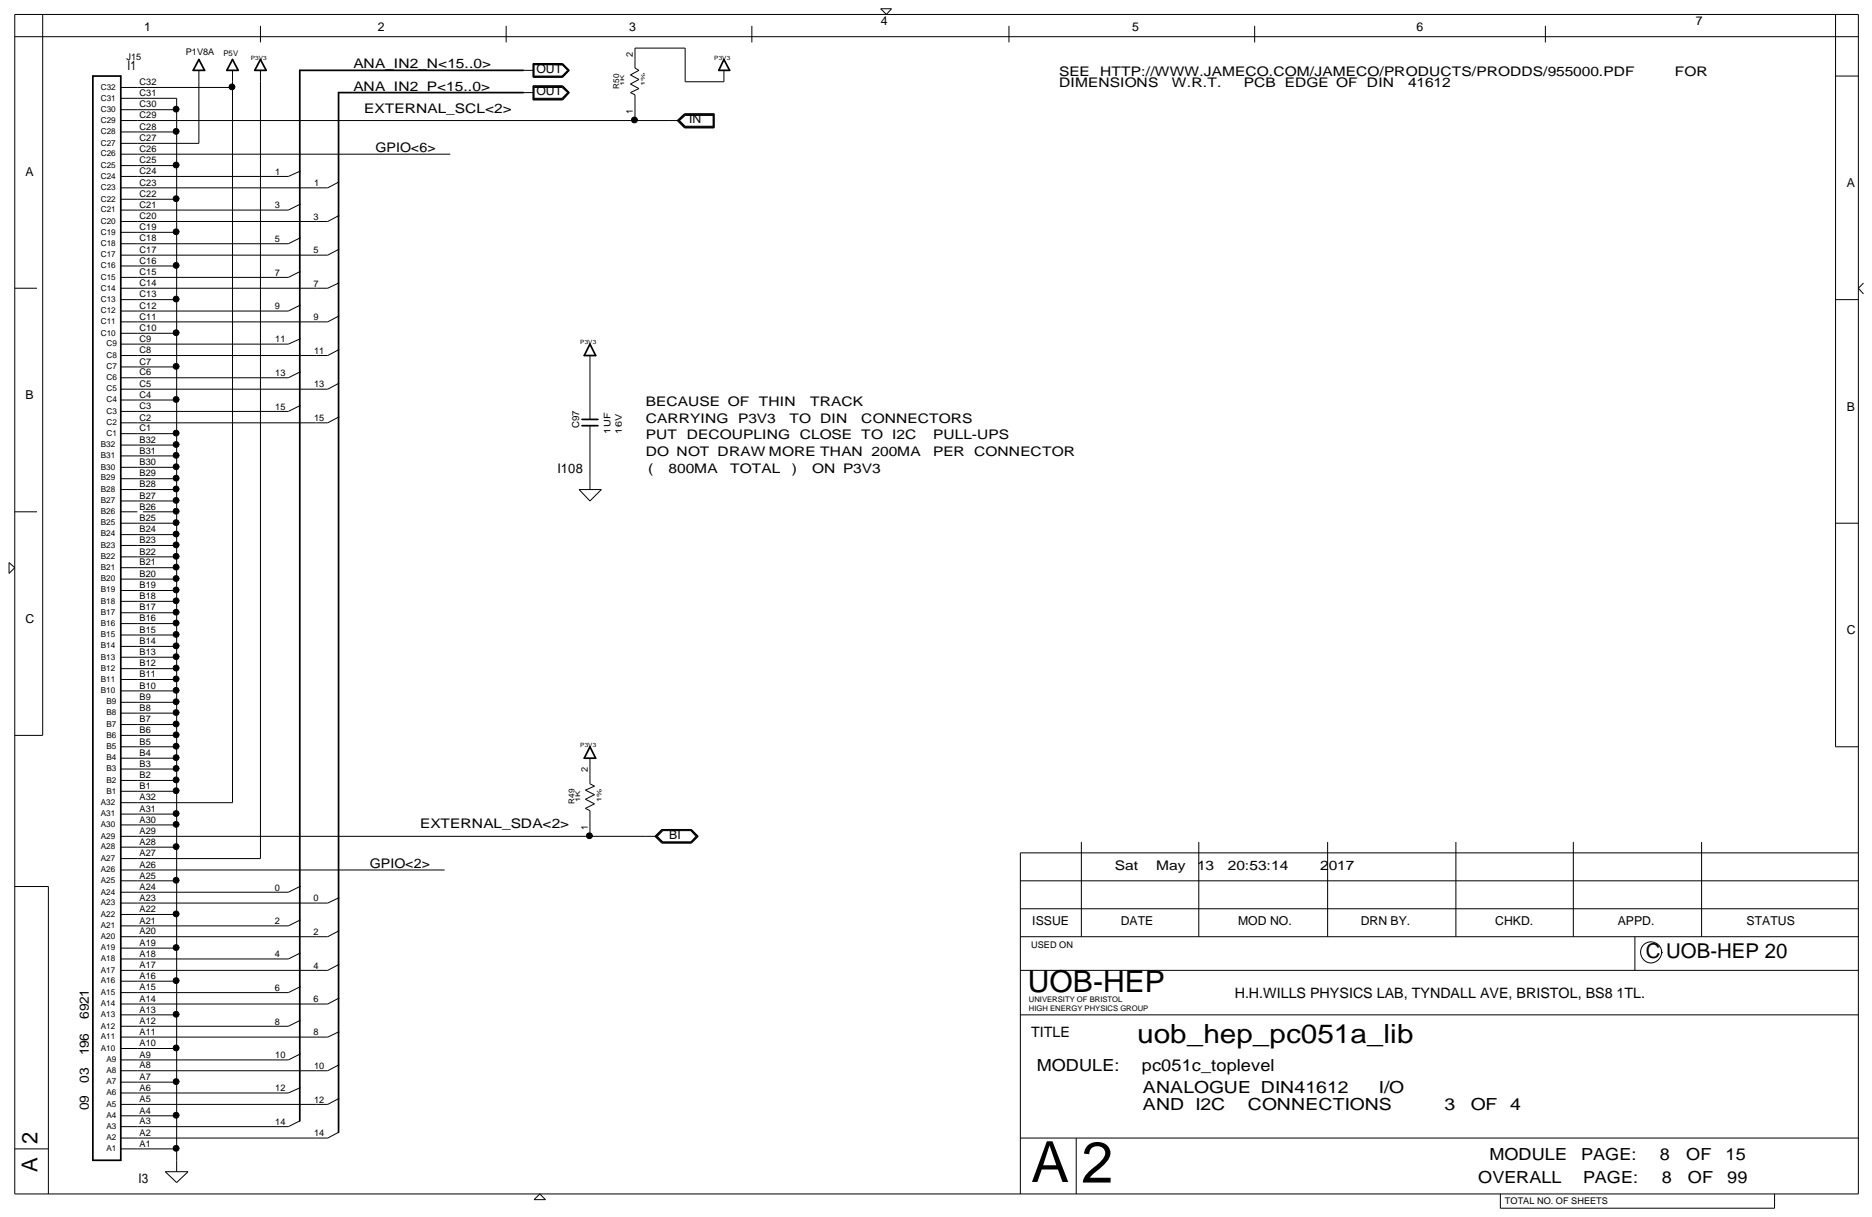
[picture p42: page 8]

BECAUSE OF THIN TRACK
CARRYING P3V3 TO DIN CONNECTORS
PUT DECOUPLING CLOSE TO I2C PULL-UPS
DO NOT DRAW MORE THAN 200MA PER CONNECTOR
( 800MA TOTAL ) ON P3V3

ISSUE | DATE | MOD NO. | DRN BY. | CHKD. | APPD. | STATUS

USED ON | C UOB-HEP 20

09 03 196 6921UNIVERSITY OF BRISTOL HIGH ENERGY PHYSICS GROUP

H.H.WILLS PHYSICS LAB, TYNDALL AVE, BRISTOL, BS8 1TL.

TOTAL NO. OF SHEETS

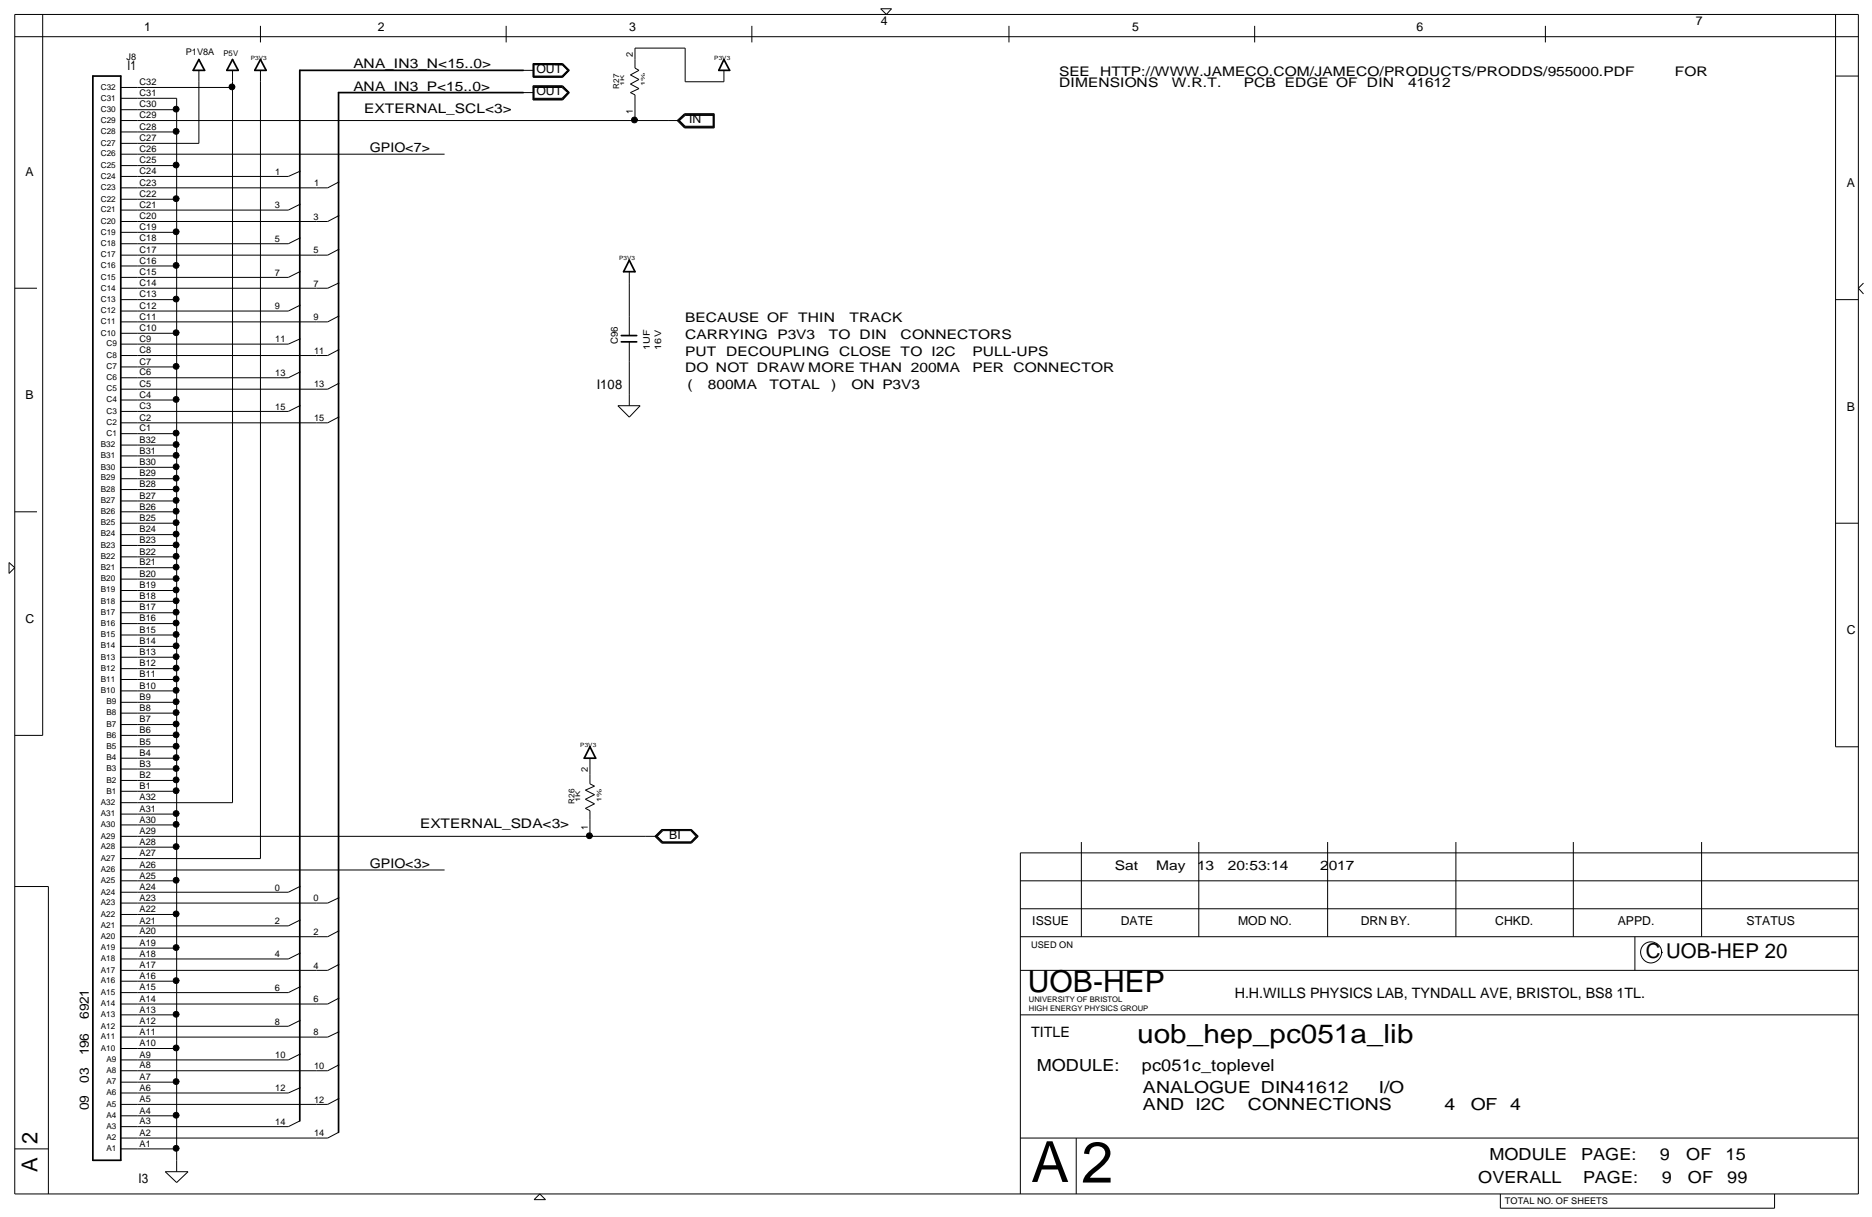
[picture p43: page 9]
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

ISSUE | DATE | MOD NO. | DRN BY. | CHKD. | APPD. | STATUS

USED ON | C UOB-HEP 20

H.H.WILLS PHYSICS LAB, TYNDALL AVE, BRISTOL, BS8 1TL.

TOTAL NO. OF SHEETS

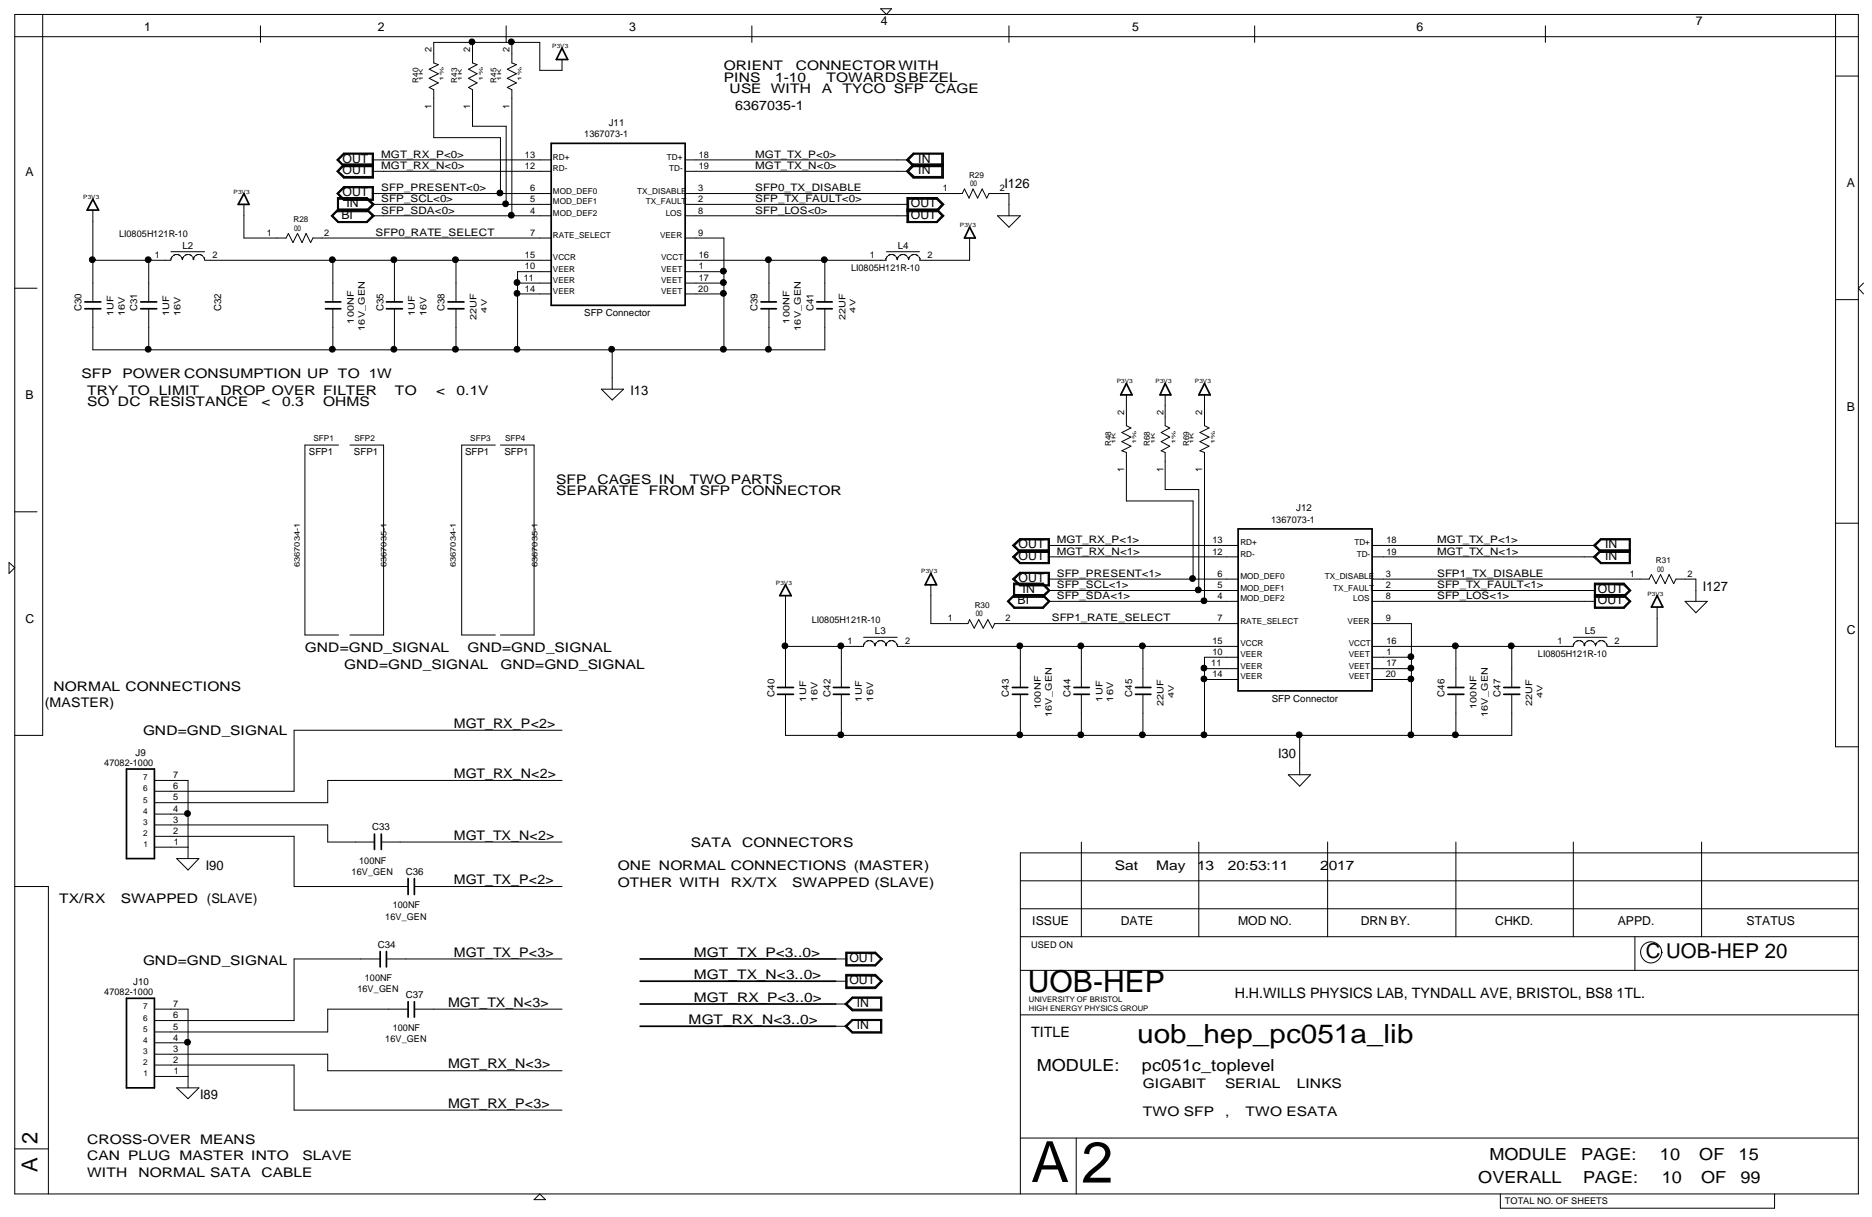
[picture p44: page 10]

ORIENT CONNECTORWITH
USE WITH A TYCO SFP CAGE

IN SFP_SDA<0> | 4 | 8 SFP_LOS<0> | OUT

SFP POWER CONSUMPTION UP TO 1W

SFP CAGES IN TWO PARTS
SEPARATE FROM SFP CONNECTOR

IN SFP_SCL<1> SFP_SDA<1> | 5 4 | 2 SFP_TX_FAULT<1> 8 SFP_LOS<1> | OUT

10 | 1
11 | 17
14 | 20

ONE NORMAL CONNECTIONS (MASTER)
OTHER WITH RX/TX SWAPPED (SLAVE)

Sat May 13 20:53:11 | 2017

ISSUE | DATE | MOD NO. | DRN BY. | CHKD. | APPD. | STATUS

USED ON | C UOB-HEP 20

H.H.WILLS PHYSICS LAB, TYNDALL AVE, BRISTOL, BS8 1TL.

TWO SFP , TWO ESATA

CROSS-OVER MEANS
CAN PLUG MASTER INTO SLAVE
WITH NORMAL SATA CABLE

TOTAL NO. OF SHEETS

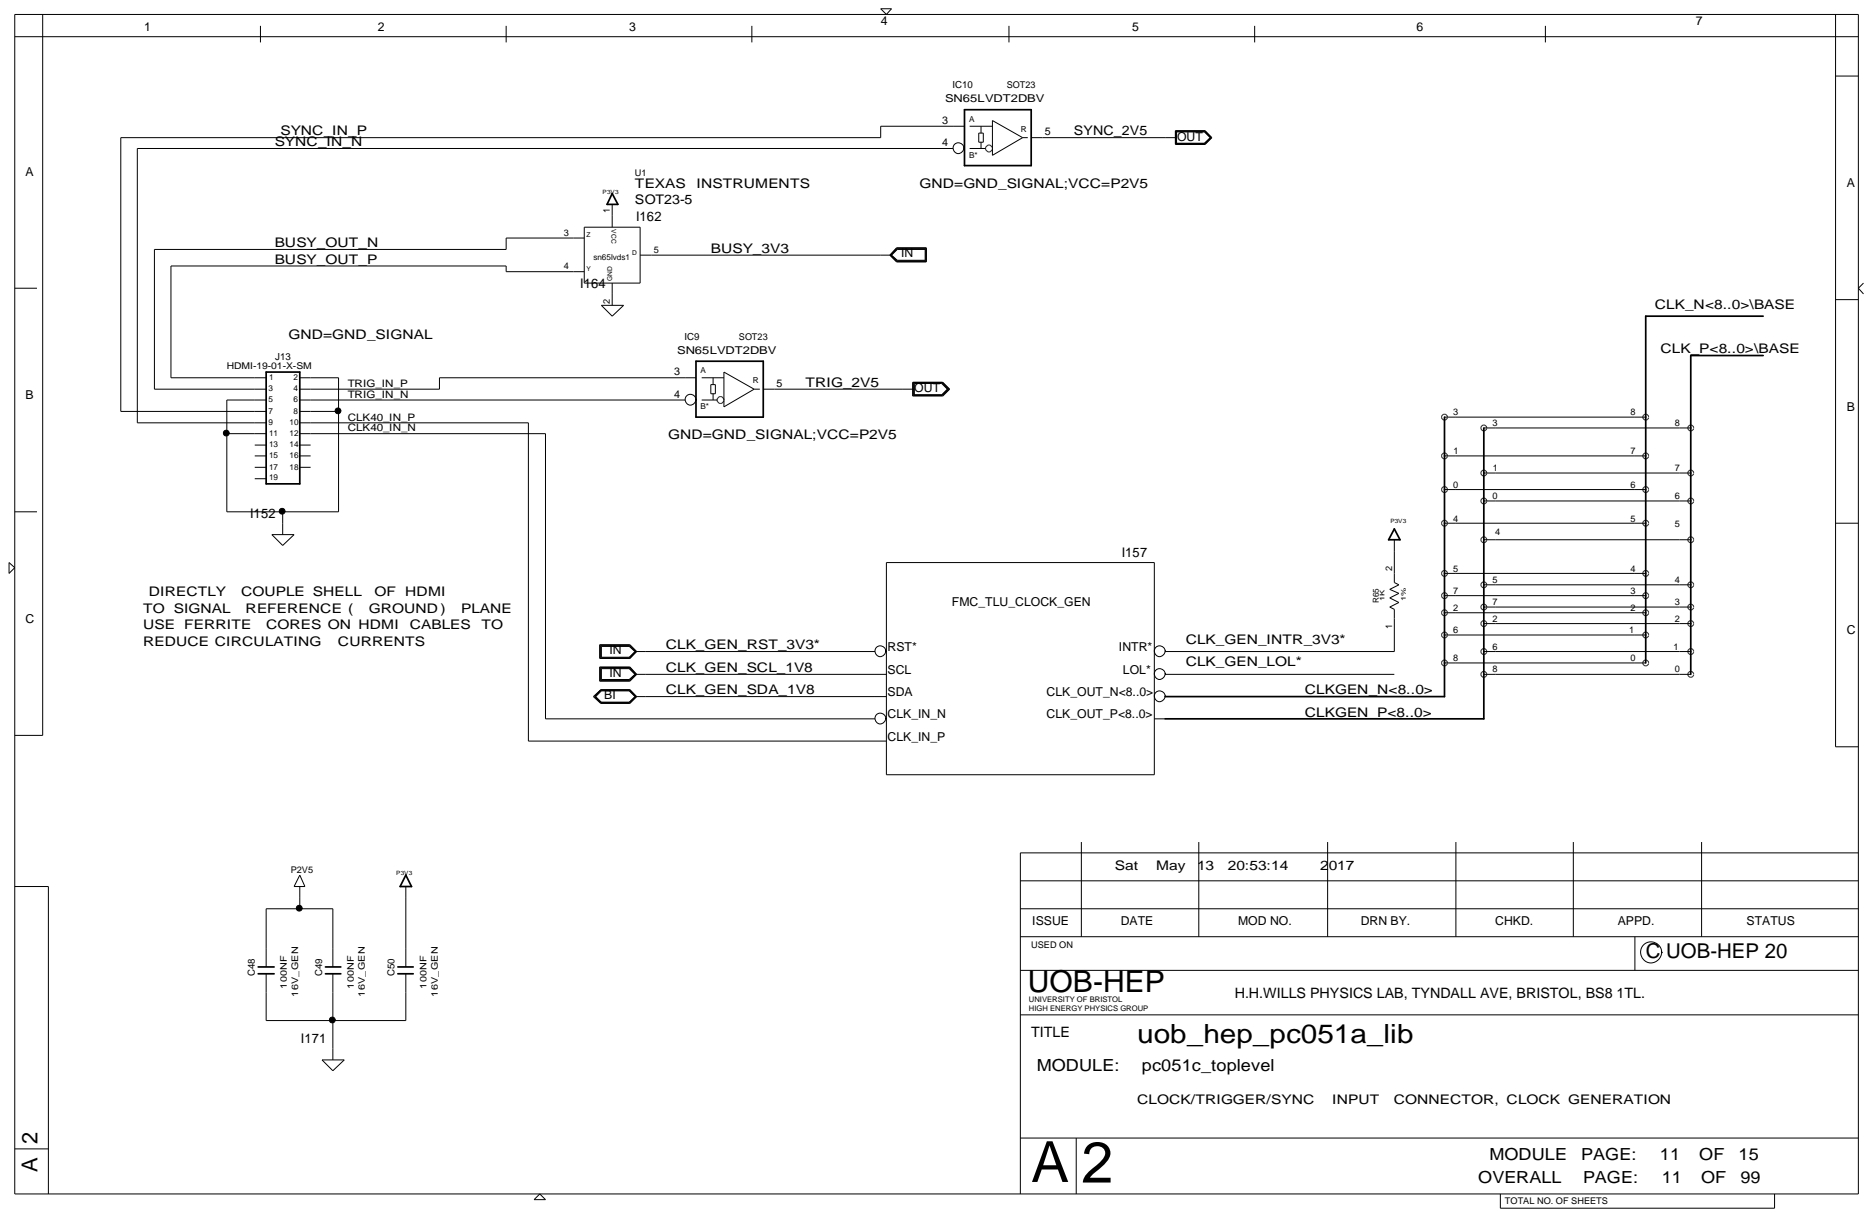
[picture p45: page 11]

DIRECTLY COUPLE SHELL OF HDMI
TO SIGNAL REFERENCE ( GROUND ) PLANE
USE FERRITE CORES ON HDMI CABLES TO
REDUCE CIRCULATING CURRENTS

ISSUE | DATE | MOD NO. | DRN BY. | CHKD. | APPD. | STATUS

USED ON | C UOB-HEP 20

H.H.WILLS PHYSICS LAB, TYNDALL AVE, BRISTOL, BS8 1TL.

CLOCK/TRIGGER/SYNC INPUT CONNECTOR, CLOCK GENERATION

TOTAL NO. OF SHEETS

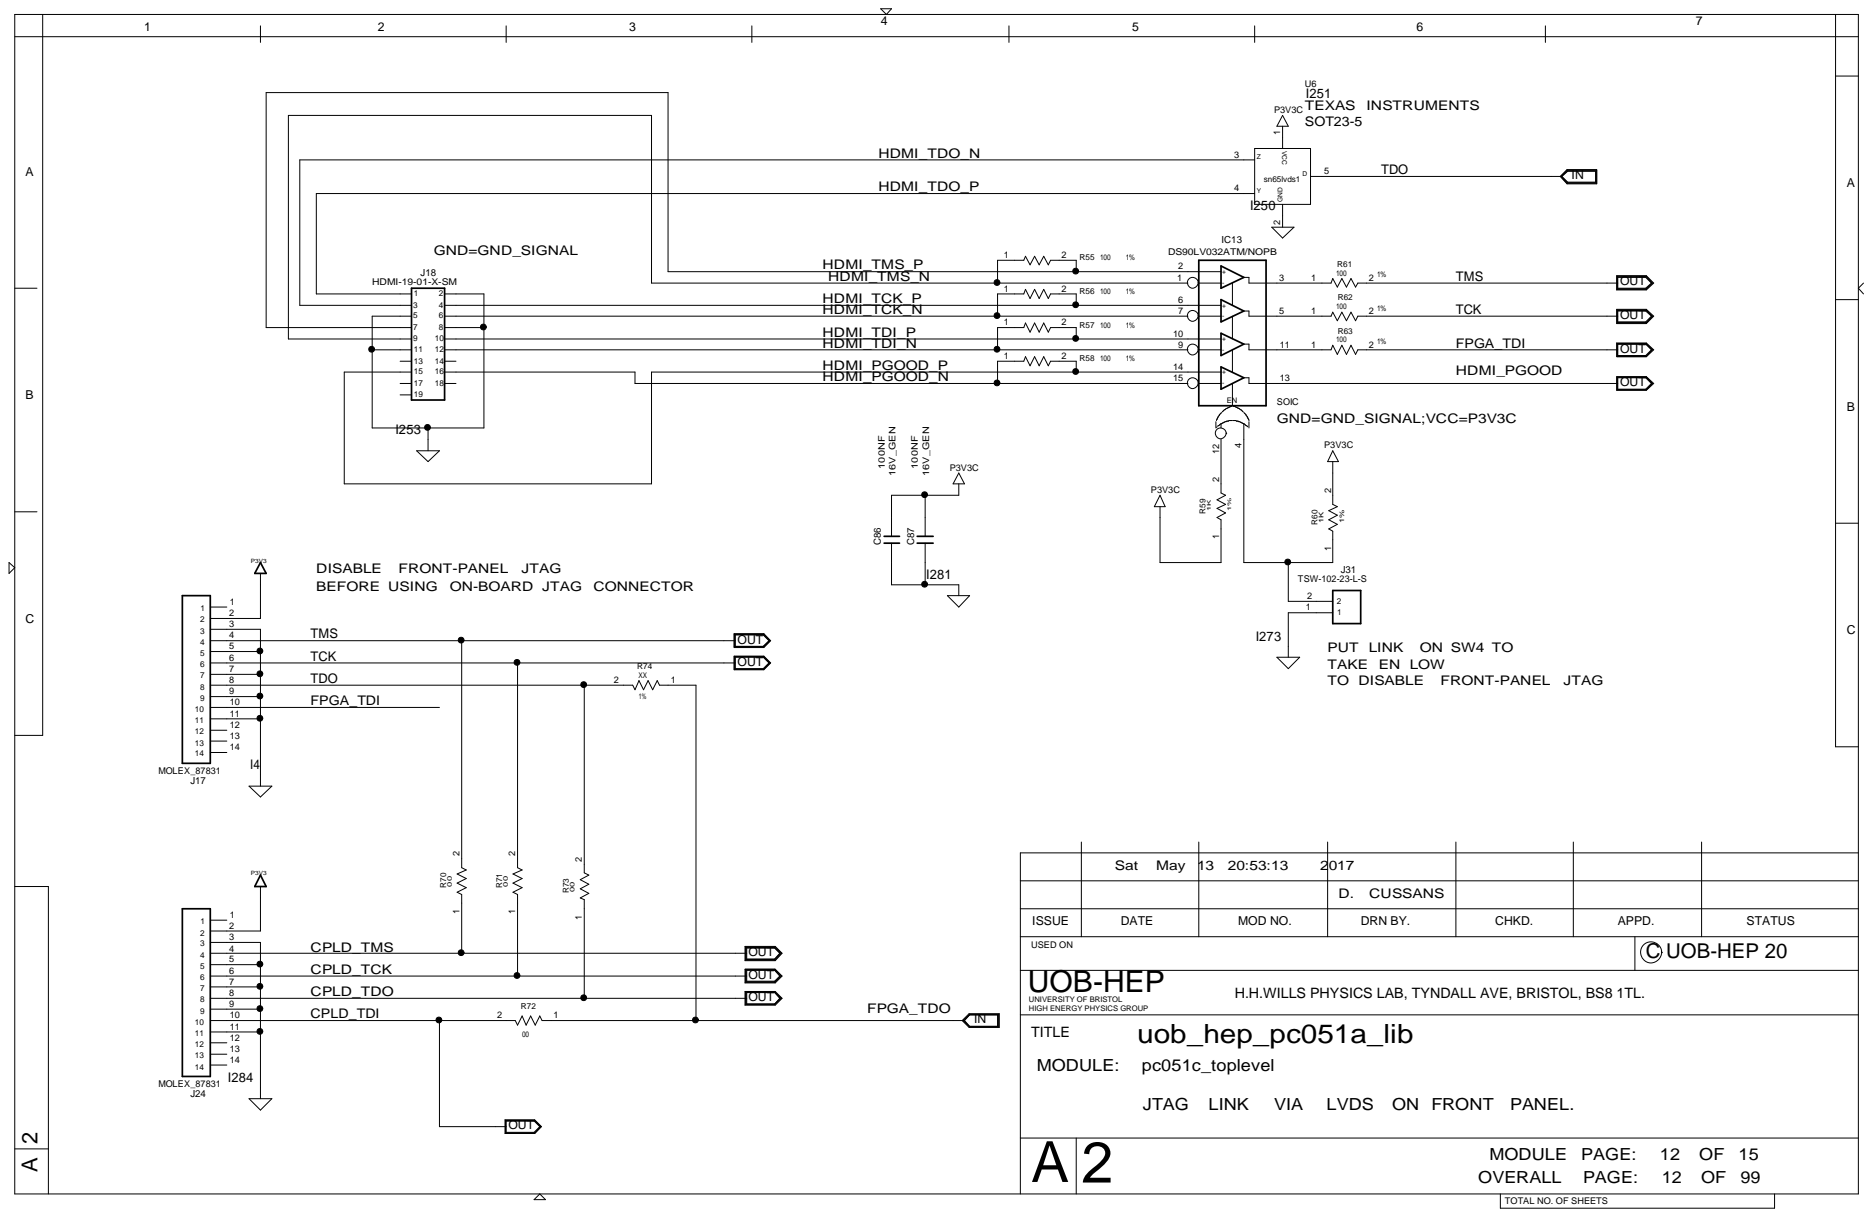
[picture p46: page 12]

HDMI_TDO_P 4

J18 HDMI-19-01-X-SM | IC13 DS90LV032ATM/NOPB 1 2 R55 100 1%

DISABLE FRONT-PANEL JTAG
BEFORE USING ON-BOARD JTAG CONNECTOR

PUT LINK ON SW4 TO
TAKE EN LOW
TO DISABLE FRONT-PANEL JTAG

Sat May 13 20:53:13 | 2017

D. CUSSANS

H.H.WILLS PHYSICS LAB, TYNDALL AVE, BRISTOL, BS8 1TL.

TOTAL NO. OF SHEETS

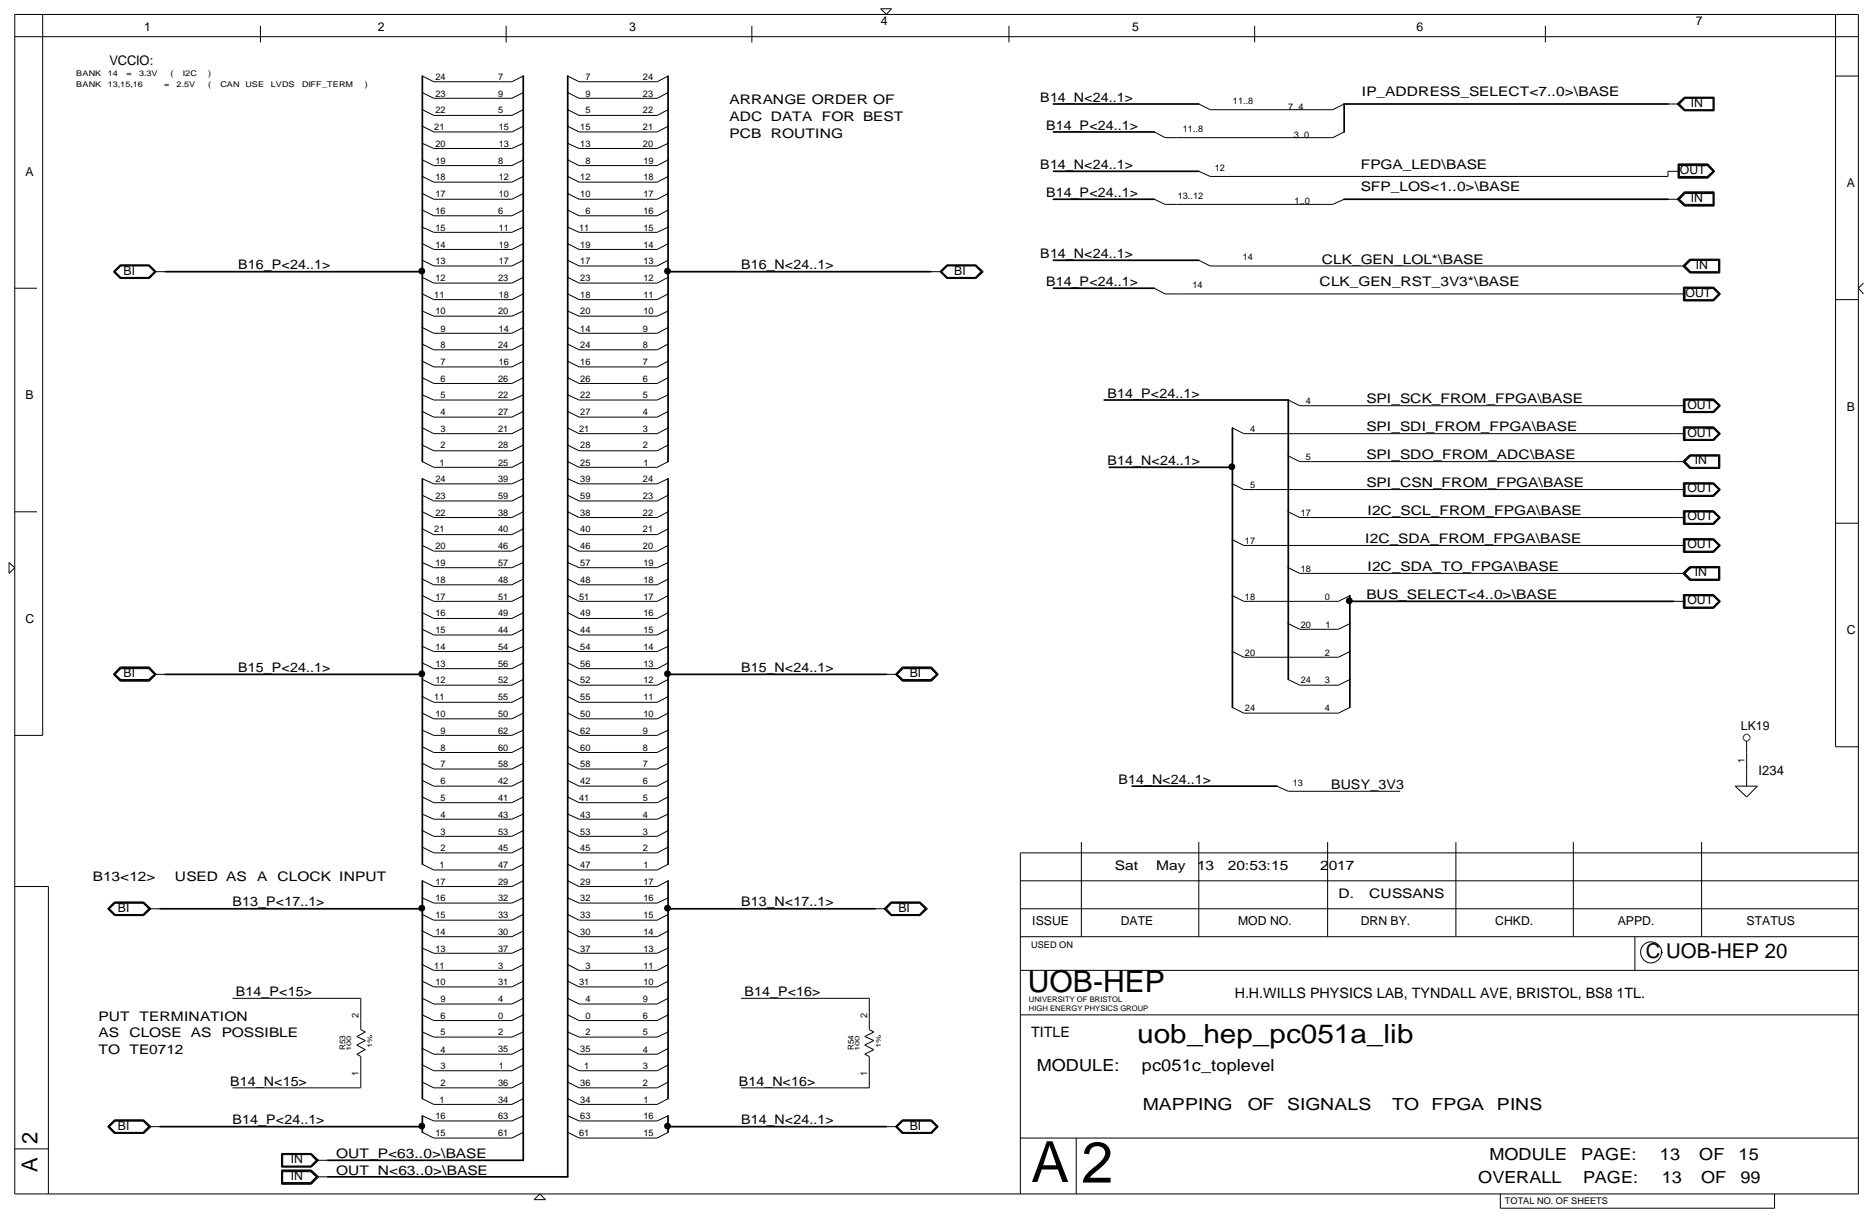
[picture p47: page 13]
USED AS A CLOCK INPUT; VCCIO:; BANK 14 = 3.3V; BANK 13,15,16; ( CAN USE LVDS DIFF_TERM; OVERALL PAGE:; MODULE PAGE:; uob_hep_pc051a_lib; SPI_SDO_FROM_ADC\BASE; SPI_SCK_FROM_FPGA\BASE; I2C_SCL_FROM_FPGA\BASE; I2C_SDA_TO_FPGA\BASE; I2C_SDA_FROM_FPGA\BASE; SPI_CSN_FROM_FPGA\BASE; SPI_SDI_FROM_FPGA\BASE; BUSY_3V3 B14_N<24..1>; CLK_GEN_RST_3V3*\BASE; CLK_GEN_LOL*\BASE; FPGA_LED\BASE; SFP_LOS<1..0>\BASE B14_P<24..1>; IP_ADDRESS_SELECT<7..0>\BASE B14_N<24..1>; BUS_SELECT<4..0>\BASE; OUT_P<63..0>\BASE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

ARRANGE ORDER OF
ADC DATA FOR BEST
PCB ROUTING

Sat May 13 20:53:15 | 2017

D. CUSSANS

ISSUE | DATE | MOD NO. | DRN BY. | CHKD. | APPD. | STATUS

USED ON | C UOB-HEP 20

UNIVERSITY OF BRISTOL
HIGH ENERGY PHYSICS GROUP
TITLE
MODULE: pc051c_toplevel

H.H.WILLS PHYSICS LAB, TYNDALL AVE, BRISTOL, BS8 1TL.

PUT TERMINATION
AS CLOSE AS POSSIBLE

MAPPING OF SIGNALS TO FPGA PINS

TOTAL NO. OF SHEETS

MUST *NOT* SHUTDOWNWHEN PGOOD IS LOW

IN SPI_SDO_FROM_ADC\BASE A4 | ADC_SDOB<7..0> | OUT
OUT IN | SPI_CSN_FROM_FPGA\BASE SPI_SDI_FROM_FPGA\BASE A5 | OUT
IN H1 | ADC_CSB<7..0> ADC_SDI<7..0> | OUT

IN I2C_SDA_TO_FPGA\BASE A8 | OUT

IN CLK_CPLD_TTL P5 | CPLD_LEDS<3..0> SFP_TX_FAULT<1..0> | OUT

IN POR_I D3 | B5 RESIN | OUT

IN | B7 PGOOD3V3 | OUT

Sat May 13 20:53:13 | 2017

D. CUSSANS

ISSUE | DATE | MOD NO. | DRN BY. | CHKD. | APPD. | STATUS

USED ON | C UOB-HEP 20

H.H.WILLS PHYSICS LAB, TYNDALL AVE, BRISTOL, BS8 1TL.

CPLD THAT MULTIPLEXES I2C AND SPI BUSES
TEMPERATURE MONITOR , POWER-ON-RESET , UNIQUE ID

TOTAL NO. OF SHEETS

- FEED 40MHZ EXTERNAL CLOCK DIRECT TO FPGA
NOT INTO CLKIN2 PINS (ASK DMN)

USE INTERNAL CLOCK GENERATOR
FOR MGT CLOCK. ( ASK DMN )

D. CUSSANS

ISSUE | DATE | MOD NO. | DRN BY. | CHKD. | APPD. | STATUS

H.H.WILLS PHYSICS LAB, TYNDALL AVE, BRISTOL, BS8 1TL.

LEVEL FOR POWER GOOD SIGNAL FROM TRENZ BOARD

TOTAL NO. OF SHEETS

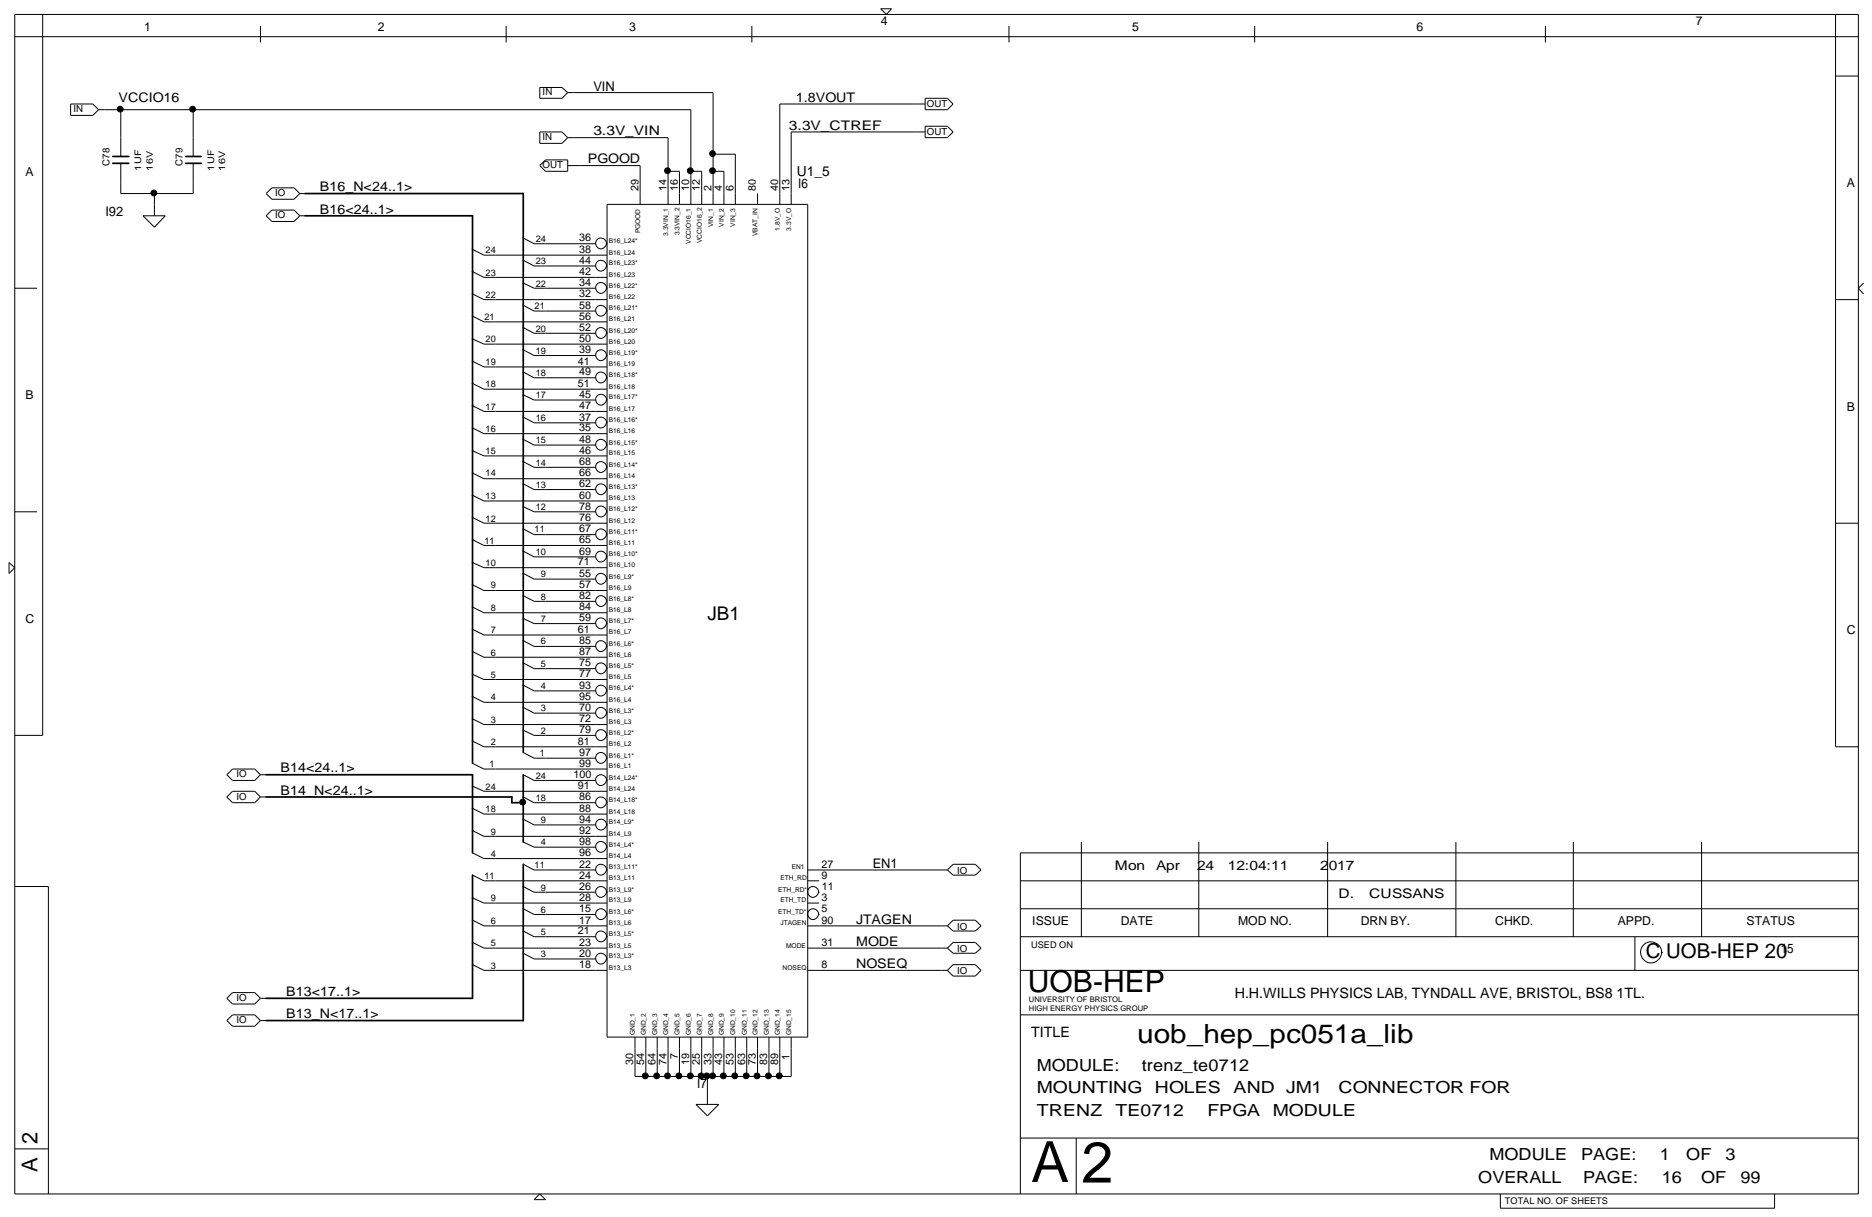
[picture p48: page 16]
TRENZ TE0712; FPGA MODULE; OVERALL PAGE:; MODULE PAGE:; uob_hep_pc051a_lib; PGOOD; NOSEQ; MODE; JTAGEN; 3.3V_VIN; 1.8VOUT; 3.3V_CTREF; VIN; VCCIO16; ETH_TD*; ETH_TD; ETH_RD*; ETH_RD; VIN_1; VIN_2; VIN_3; VCCIO16_1; VCCIO16_2; VBAT_IN; GND_1; GND_2; GND_3; GND_4; GND_5; GND_6; GND_7; GND_8; GND_9; GND_10; GND_11; GND_12; GND_13; GND_14; GND_15; 3.3VIN_1; 3.3VIN_2; OUT; UOB-HEP

Mon Apr 24 12:04:11 | 2017

D. CUSSANS

ISSUE | DATE | MOD NO. | DRN BY. | CHKD. | APPD. | STATUS
USED ON | C UOB-HEP 20 15

UNIVERSITY OF BRISTOL
HIGH ENERGY PHYSICS GROUP
TITLE

H.H.WILLS PHYSICS LAB, TYNDALL AVE, BRISTOL, BS8 1TL.

MODULE: trenz_te0712
MOUNTING HOLES AND JM1 CONNECTOR FOR

TOTAL NO. OF SHEETS

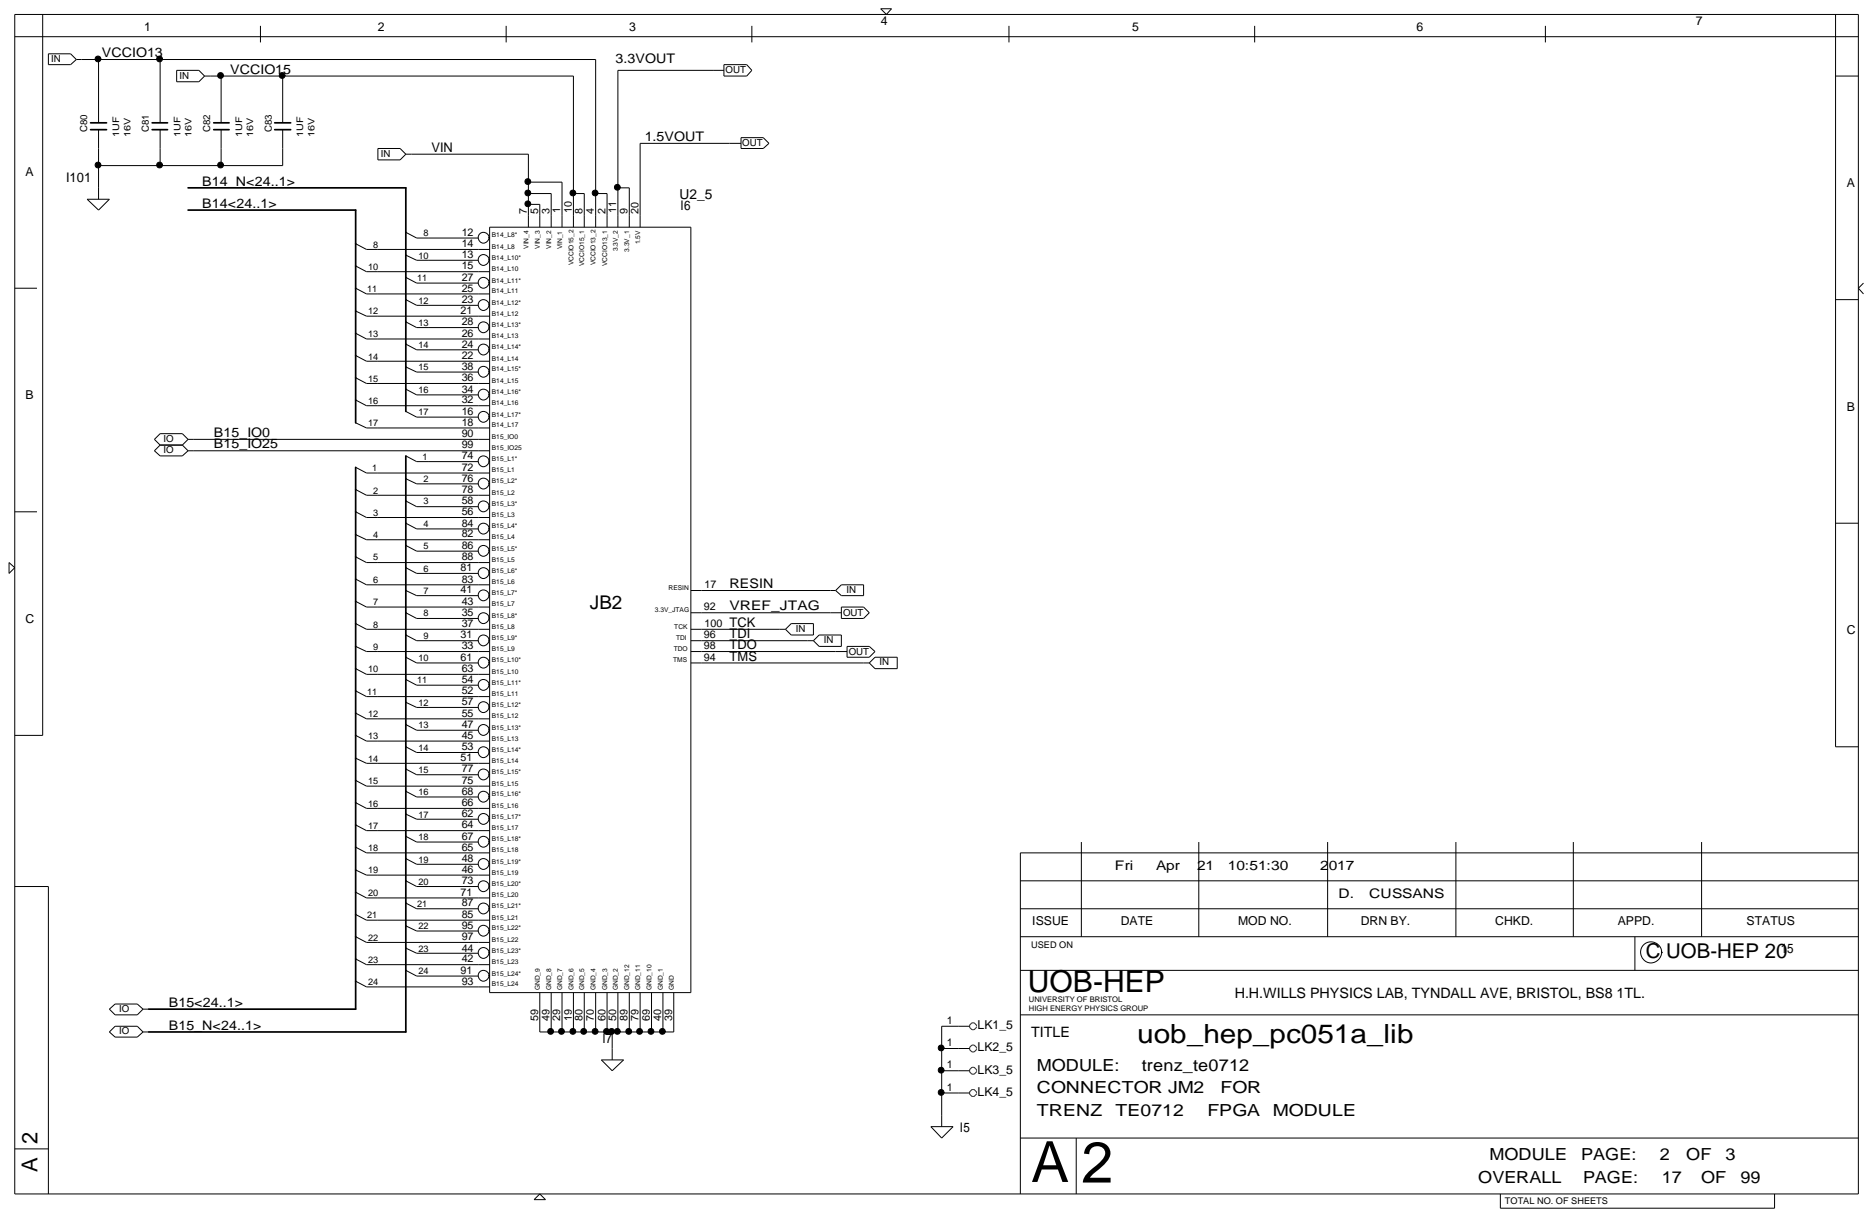
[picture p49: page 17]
TRENZ TE0712; FPGA MODULE; OVERALL PAGE:; MODULE PAGE:; uob_hep_pc051a_lib; VIN; VCCIO15; VCCIO13; 3.3VOUT; 1.5VOUT; TDO; TDI; RESIN VREF_JTAG TCK; TMS; TCK; RESIN; 3.3V_JTAG; VIN_4; VIN_3; VIN_2; VIN_1; VCCIO15_2; VCCIO15_1; VCCIO13_2; VCCIO13_1; GND_9; GND_8; GND_7; GND_6; GND_5; GND_4; GND_3; GND_2; GND_12; GND_11; GND_10; GND_1; GND; OUT; UOB-HEP

Fri Apr 21 10:51:30 | 2017

D. CUSSANS

ISSUE | DATE | MOD NO. | DRN BY. | CHKD. | APPD. | STATUS
USED ON | C UOB-HEP 20 15

UNIVERSITY OF BRISTOL
HIGH ENERGY PHYSICS GROUP
TITLE
MODULE: trenz_te0712
CONNECTOR JM2 FOR

H.H.WILLS PHYSICS LAB, TYNDALL AVE, BRISTOL, BS8 1TL.

TOTAL NO. OF SHEETS

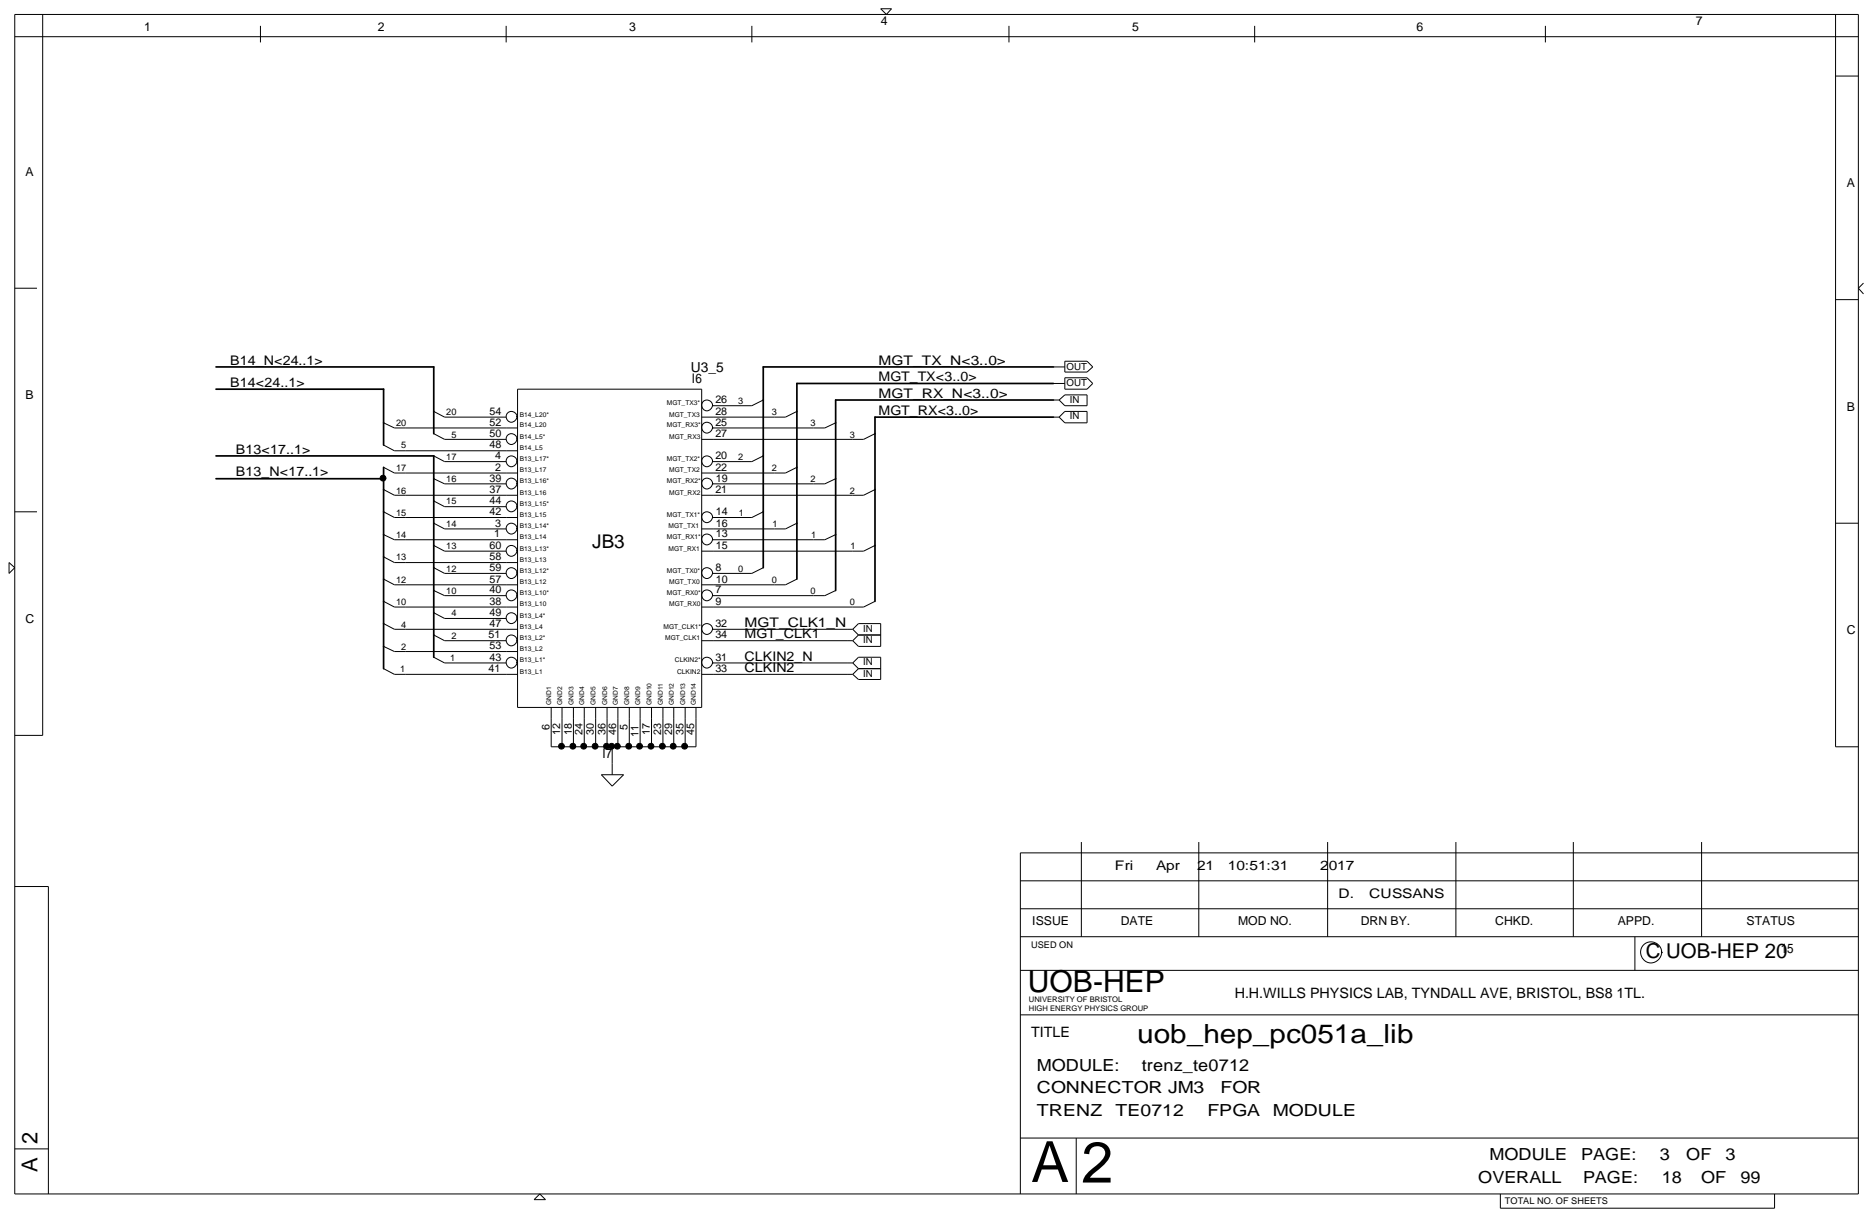
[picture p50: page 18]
TRENZ TE0712; FPGA MODULE; OVERALL PAGE:; MODULE PAGE:; uob_hep_pc051a_lib; MGT_CLK1_N MGT_CLK1 CLKIN2_N CLKIN2; MGT_RX<3..0>; MGT_RX_N<3..0>; MGT_TX<3..0>; MGT_TX_N<3..0>; MGT_TX3* MGT_TX3 MGT_RX3* MGT_RX3; MGT_TX2* MGT_TX2 MGT_RX2* MGT_RX2; MGT_TX1* MGT_TX1 MGT_RX1* MGT_RX1; MGT_TX0* MGT_TX0 MGT_RX0* MGT_RX0; MGT_CLK1* MGT_CLK1; CLKIN2* CLKIN2; GND1; GND2; GND3; GND4; GND5; GND6; GND7; GND8; GND9; GND10; GND11; GND12; GND13; GND14; OUT; UOB-HEP

Fri Apr 21 10:51:31 | 2017

D. CUSSANS

ISSUE | DATE | MOD NO. | DRN BY. | CHKD. | APPD. | STATUS
USED ON | C UOB-HEP 20 15

UNIVERSITY OF BRISTOL
HIGH ENERGY PHYSICS GROUP
TITLE
MODULE: trenz_te0712
CONNECTOR JM3 FOR

H.H.WILLS PHYSICS LAB, TYNDALL AVE, BRISTOL, BS8 1TL.

TOTAL NO. OF SHEETS

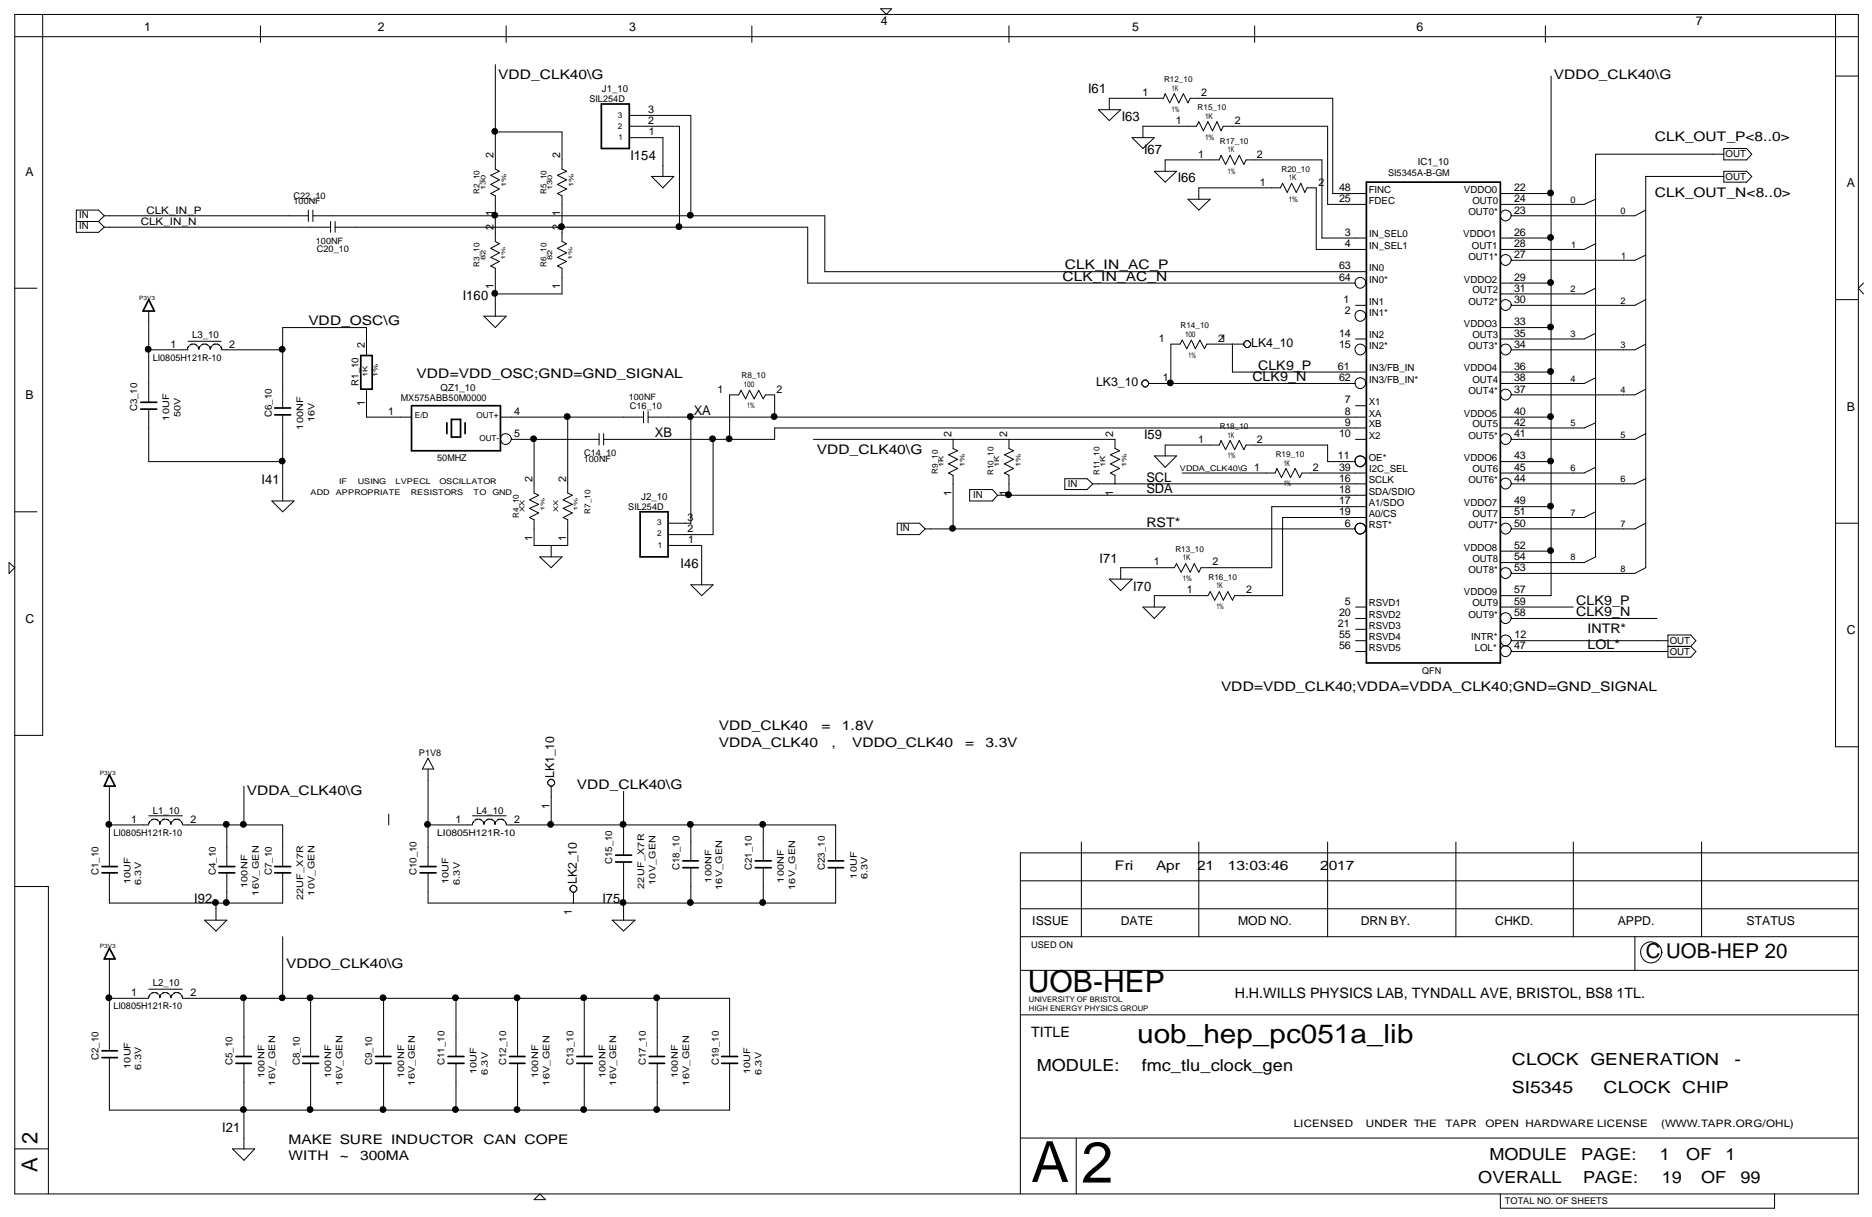
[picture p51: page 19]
VDDA_CLK40 , VDDO_CLK40 = 3.3V; CLOCK CHIP; CLOCK GENERATION -; VDD_CLK40 = 1.8V; USING LVPECL OSCILLATOR; Fri; Apr 21 13:03:46; OVERALL PAGE:; MODULE PAGE:; uob_hep_pc051a_lib; CLK9_N; CLK9_P; VDDO_CLK40\G; VDD_CLK40\G; VDDA_CLK40\G; VDD_OSC\G; CLK_IN_AC_P CLK_IN_AC_N; CLK_IN_N; CLK_IN_P; INTR* LOL*; SCL SDA; RST*; CLK_OUT_N<8..0>; CLK_OUT_P<8..0>; 16V_GEN; 10V_GEN; VDD=VDD_OSC;GND=GND_SIGNAL; 50MHZ; MX575ABB50M0000; SIL254D; QFN; OUT-; OUT; RSVD3 RSVD4 RSVD5; RSVD1 RSVD2; IN_SEL1; IN_SEL0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

E/D | OUT+

SIL254D | 1 2

ADD APPROPRIATE RESISTORS TO GND

VDD=VDD_CLK40;VDDA=VDDA_CLK40;GND=GND_SIGNAL

ISSUE | DATE | MOD NO. | DRN BY. | CHKD. | APPD. | STATUS

USED ON | C UOB-HEP 20

UNIVERSITY OF BRISTOL
HIGH ENERGY PHYSICS GROUP
TITLE
MODULE: fmc_tlu_clock_gen

H.H.WILLS PHYSICS LAB, TYNDALL AVE, BRISTOL, BS8 1TL.

LICENSED UNDER THE TAPR OPEN HARDWARE LICENSE (WWW.TAPR.ORG/OHL)

MAKE SURE INDUCTOR CAN COPE
WITH ~ 300MA

TOTAL NO. OF SHEETS

IN CSB M5 | J10 J9 | 100
IN | R23_1 1%

Fri Apr 21 10:51:29 | 2017

D. CUSSANS

ISSUE | DATE | MOD NO. | DRN BY. | CHKD. | APPD. | STATUS

H.H.WILLS PHYSICS LAB, TYNDALL AVE, BRISTOL, BS8 1TL.

TOTAL NO. OF SHEETS

AFILT+ AIN- AIN+

Fri Apr 21 10:51:29 | 2017

D. CUSSANS

ISSUE | DATE | MOD NO. | DRN BY. | CHKD. | APPD. | STATUS
USED ON | C UOB-HEP 20 15

UNIVERSITY OF BRISTOL
HIGH ENERGY PHYSICS GROUP
TITLE
MODULE: ltm9007_8chan_v2

H.H.WILLS PHYSICS LAB, TYNDALL AVE, BRISTOL, BS8 1TL.

TOTAL NO. OF SHEETS

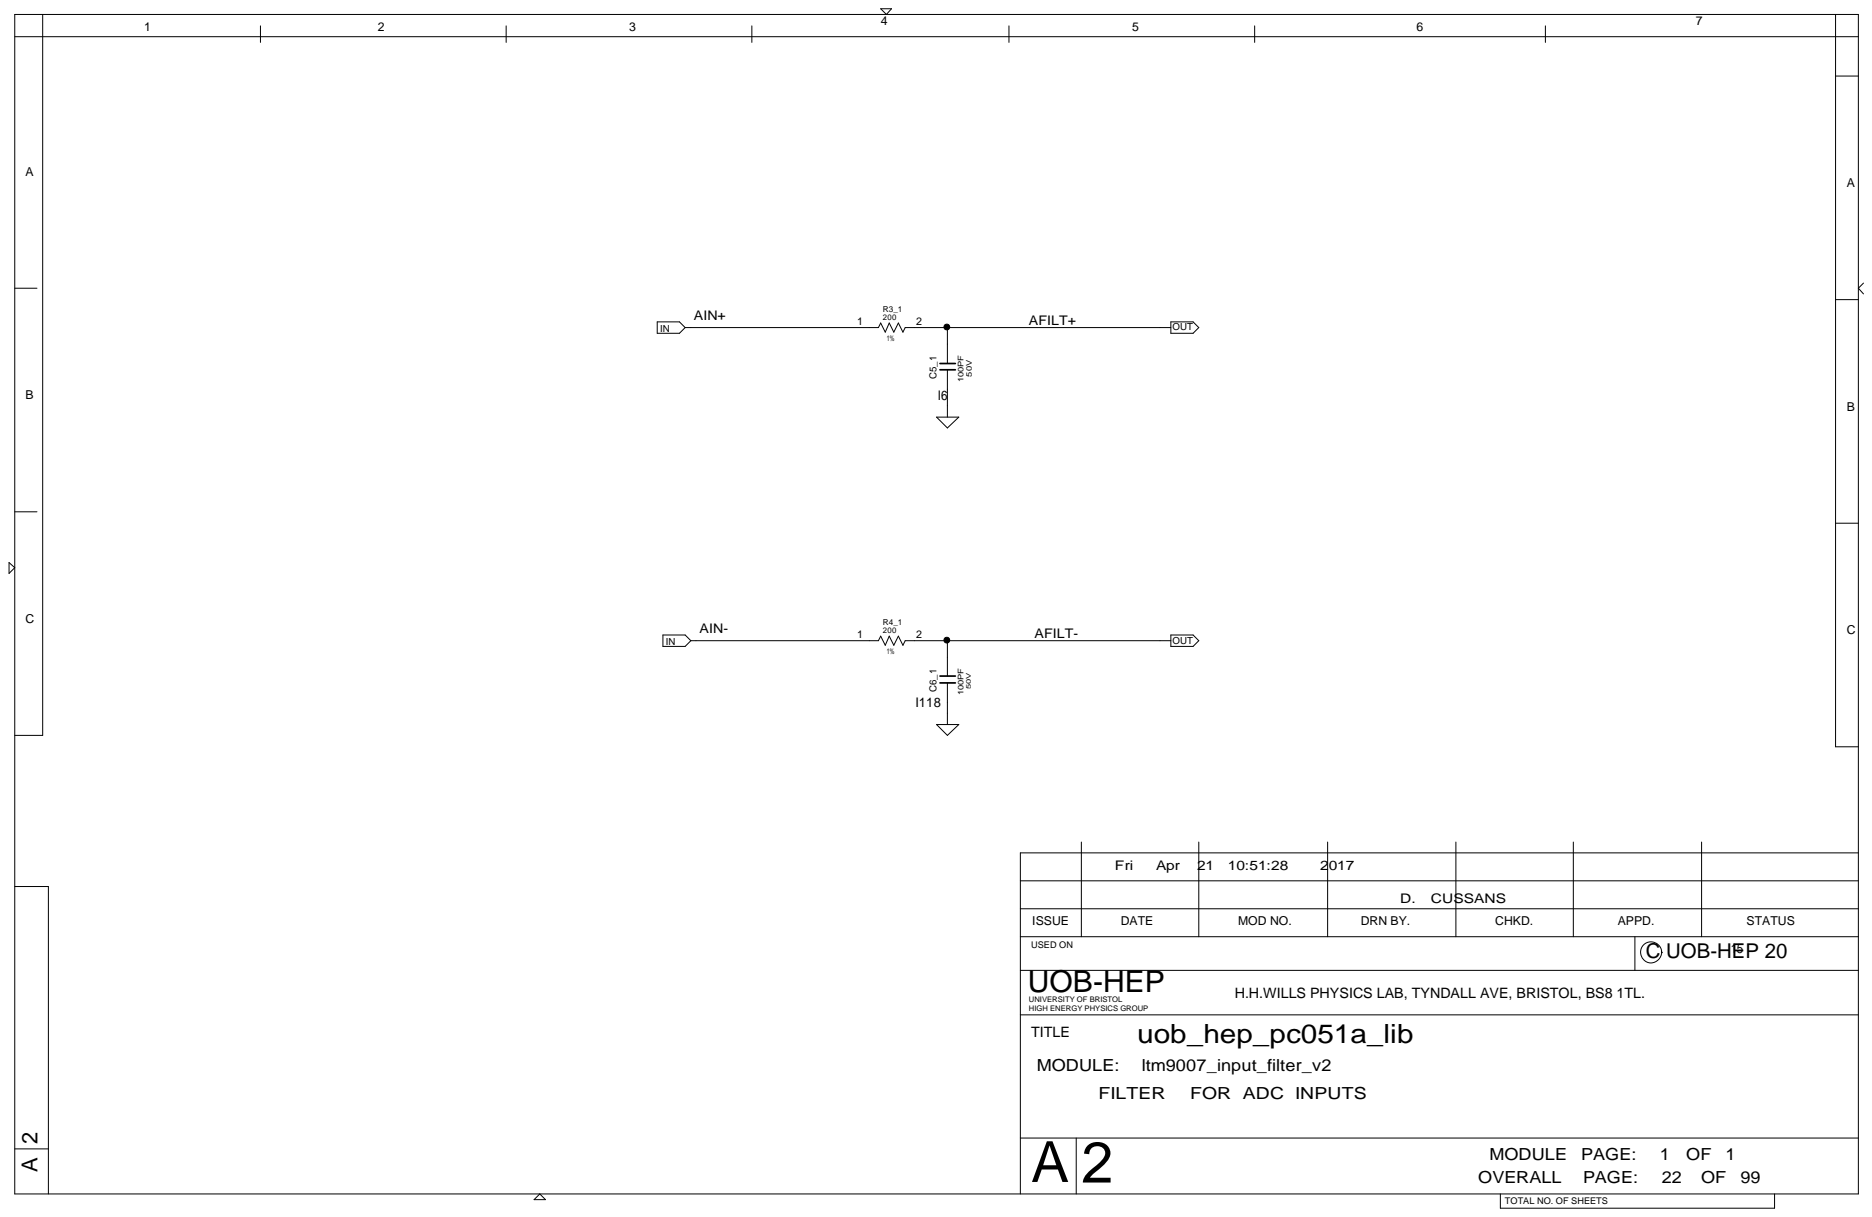
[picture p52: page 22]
FILTER; FOR ADC INPUTS; OVERALL PAGE:; MODULE PAGE:; uob_hep_pc051a_lib; AIN-; AFILT+ AFILT- AIN+; OUT; UOB-HEP

Fri Apr 21 10:51:28 | 2017

D. CUSSANS

ISSUE | DATE | MOD NO. | DRN BY. | CHKD. | APPD. | STATUS
USED ON | C UOB-HEP 20 15

UNIVERSITY OF BRISTOL
HIGH ENERGY PHYSICS GROUP
TITLE
MODULE: ltm9007_input_filter_v2

H.H.WILLS PHYSICS LAB, TYNDALL AVE, BRISTOL, BS8 1TL.

TOTAL NO. OF SHEETS

Fri Apr 21 10:51:28 | 2017

D. CUSSANS

ISSUE | DATE | MOD NO. | DRN BY. | CHKD. | APPD. | STATUS
USED ON | C UOB-HEP 20 15

UNIVERSITY OF BRISTOL
HIGH ENERGY PHYSICS GROUP
TITLE
MODULE: ltm9007_input_filter_v2

H.H.WILLS PHYSICS LAB, TYNDALL AVE, BRISTOL, BS8 1TL.

TOTAL NO. OF SHEETS

Fri Apr 21 10:51:28 | 2017

D. CUSSANS

ISSUE | DATE | MOD NO. | DRN BY. | CHKD. | APPD. | STATUS
USED ON | C UOB-HEP 20 15

UNIVERSITY OF BRISTOL
HIGH ENERGY PHYSICS GROUP
TITLE
MODULE: ltm9007_input_filter_v2

H.H.WILLS PHYSICS LAB, TYNDALL AVE, BRISTOL, BS8 1TL.

TOTAL NO. OF SHEETS

Fri Apr 21 10:51:28 | 2017

D. CUSSANS

ISSUE | DATE | MOD NO. | DRN BY. | CHKD. | APPD. | STATUS
USED ON | C UOB-HEP 20 15

UNIVERSITY OF BRISTOL
HIGH ENERGY PHYSICS GROUP
TITLE
MODULE: ltm9007_input_filter_v2

H.H.WILLS PHYSICS LAB, TYNDALL AVE, BRISTOL, BS8 1TL.

TOTAL NO. OF SHEETS

Fri Apr 21 10:51:28 | 2017

D. CUSSANS

ISSUE | DATE | MOD NO. | DRN BY. | CHKD. | APPD. | STATUS
USED ON | C UOB-HEP 20 15

UNIVERSITY OF BRISTOL
HIGH ENERGY PHYSICS GROUP
TITLE
MODULE: ltm9007_input_filter_v2

H.H.WILLS PHYSICS LAB, TYNDALL AVE, BRISTOL, BS8 1TL.

TOTAL NO. OF SHEETS

Fri Apr 21 10:51:28 | 2017

D. CUSSANS

ISSUE | DATE | MOD NO. | DRN BY. | CHKD. | APPD. | STATUS
USED ON | C UOB-HEP 20 15

UNIVERSITY OF BRISTOL
HIGH ENERGY PHYSICS GROUP
TITLE
MODULE: ltm9007_input_filter_v2

H.H.WILLS PHYSICS LAB, TYNDALL AVE, BRISTOL, BS8 1TL.

TOTAL NO. OF SHEETS

Fri Apr 21 10:51:28 | 2017

D. CUSSANS

ISSUE | DATE | MOD NO. | DRN BY. | CHKD. | APPD. | STATUS
USED ON | C UOB-HEP 20 15

UNIVERSITY OF BRISTOL
HIGH ENERGY PHYSICS GROUP
TITLE
MODULE: ltm9007_input_filter_v2

H.H.WILLS PHYSICS LAB, TYNDALL AVE, BRISTOL, BS8 1TL.

TOTAL NO. OF SHEETS

Fri Apr 21 10:51:28 | 2017

D. CUSSANS

ISSUE | DATE | MOD NO. | DRN BY. | CHKD. | APPD. | STATUS
USED ON | C UOB-HEP 20 15

UNIVERSITY OF BRISTOL
HIGH ENERGY PHYSICS GROUP
TITLE
MODULE: ltm9007_input_filter_v2

H.H.WILLS PHYSICS LAB, TYNDALL AVE, BRISTOL, BS8 1TL.

TOTAL NO. OF SHEETS

IN CSB M5 | J10 J9 | 100
IN | R23_2 1%

Fri Apr 21 10:51:29 | 2017

D. CUSSANS

ISSUE | DATE | MOD NO. | DRN BY. | CHKD. | APPD. | STATUS

H.H.WILLS PHYSICS LAB, TYNDALL AVE, BRISTOL, BS8 1TL.

TOTAL NO. OF SHEETS

AFILT+ AIN- AIN+

Fri Apr 21 10:51:29 | 2017

D. CUSSANS

ISSUE | DATE | MOD NO. | DRN BY. | CHKD. | APPD. | STATUS
USED ON | C UOB-HEP 20 15

UNIVERSITY OF BRISTOL
HIGH ENERGY PHYSICS GROUP
TITLE
MODULE: ltm9007_8chan_v2

H.H.WILLS PHYSICS LAB, TYNDALL AVE, BRISTOL, BS8 1TL.

TOTAL NO. OF SHEETS

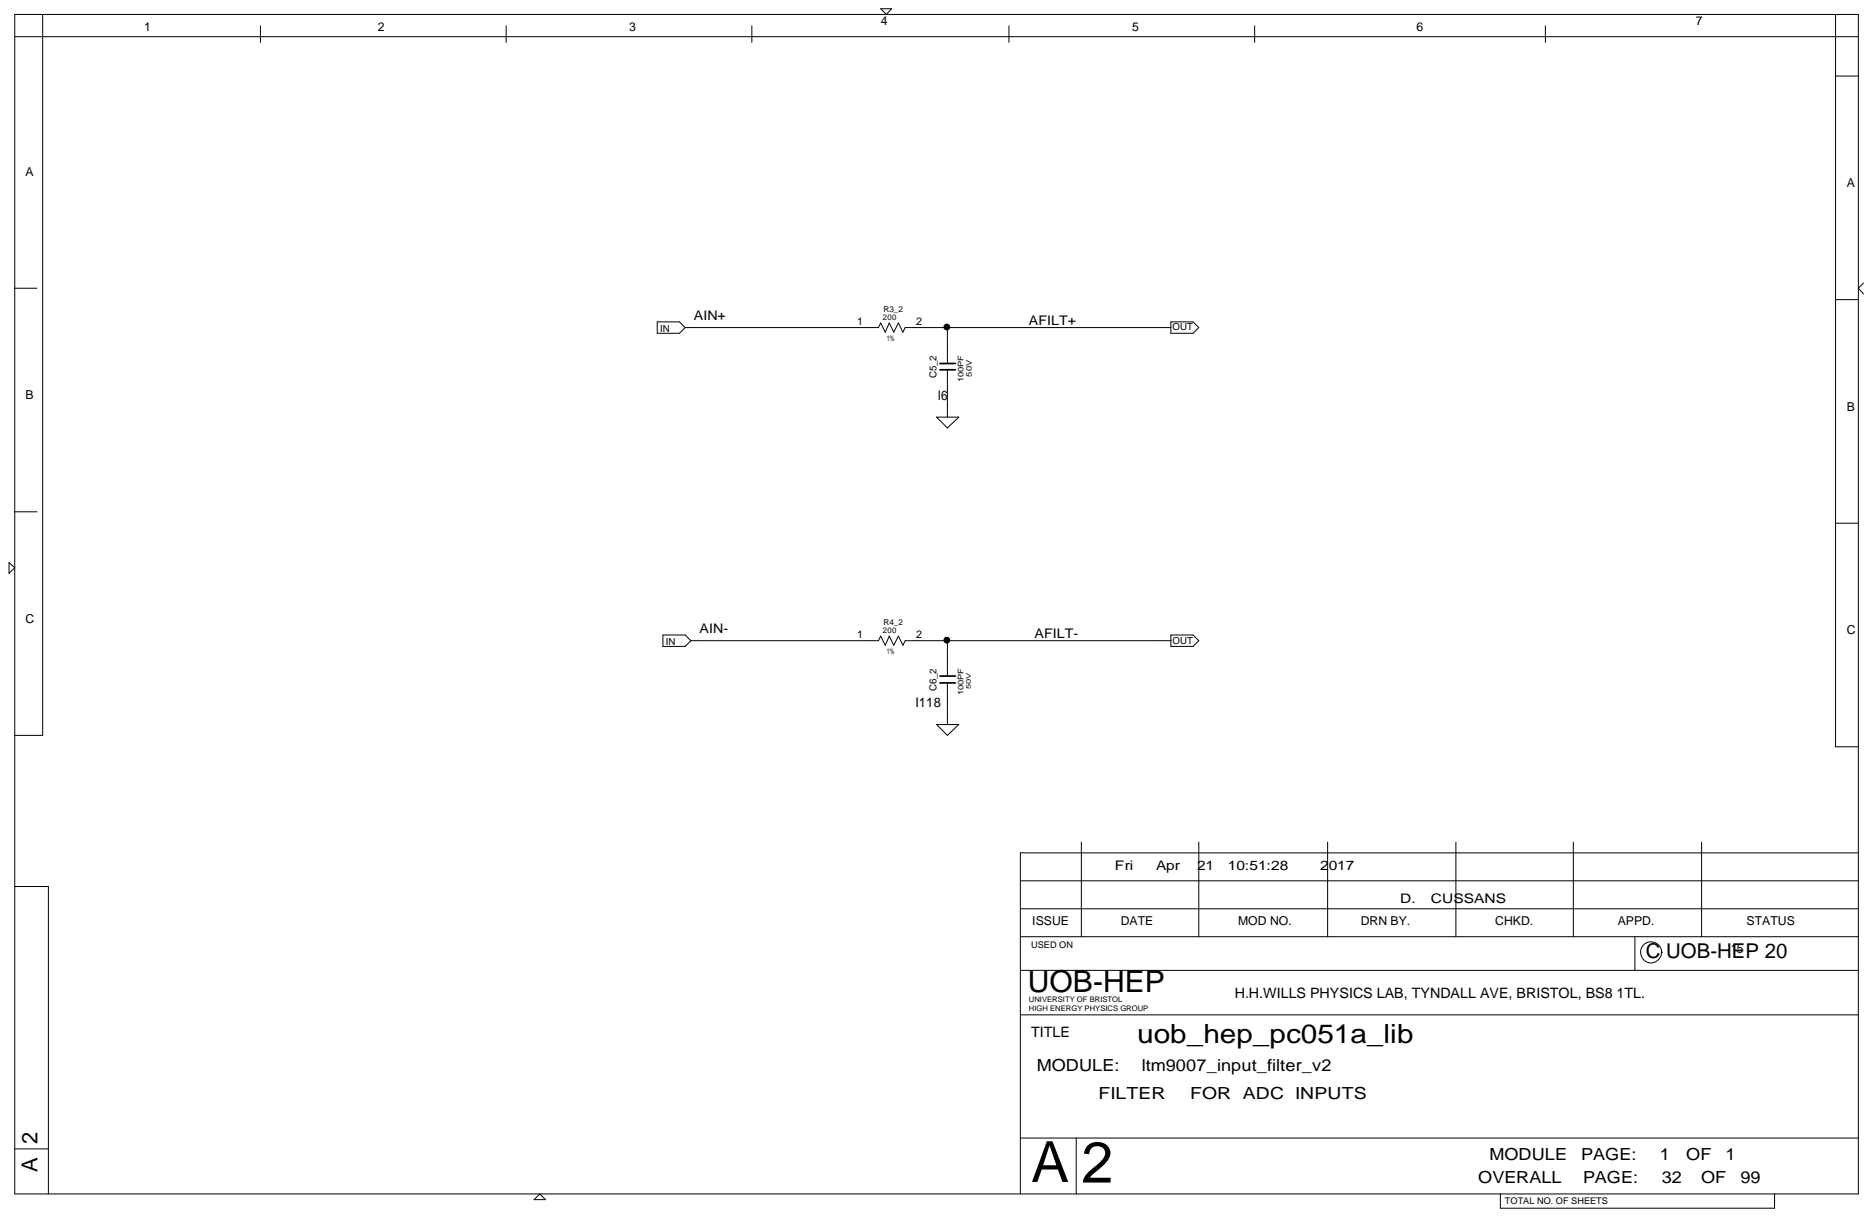
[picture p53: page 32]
FILTER; FOR ADC INPUTS; OVERALL PAGE:; MODULE PAGE:; uob_hep_pc051a_lib; AIN-; AFILT+ AFILT- AIN+; OUT; UOB-HEP

Fri Apr 21 10:51:28 | 2017

D. CUSSANS

ISSUE | DATE | MOD NO. | DRN BY. | CHKD. | APPD. | STATUS
USED ON | C UOB-HEP 20 15

UNIVERSITY OF BRISTOL
HIGH ENERGY PHYSICS GROUP
TITLE
MODULE: ltm9007_input_filter_v2

H.H.WILLS PHYSICS LAB, TYNDALL AVE, BRISTOL, BS8 1TL.

TOTAL NO. OF SHEETS

Fri Apr 21 10:51:28 | 2017

D. CUSSANS

ISSUE | DATE | MOD NO. | DRN BY. | CHKD. | APPD. | STATUS
USED ON | C UOB-HEP 20 15

UNIVERSITY OF BRISTOL
HIGH ENERGY PHYSICS GROUP
TITLE
MODULE: ltm9007_input_filter_v2

H.H.WILLS PHYSICS LAB, TYNDALL AVE, BRISTOL, BS8 1TL.

TOTAL NO. OF SHEETS

Fri Apr 21 10:51:28 | 2017

D. CUSSANS

ISSUE | DATE | MOD NO. | DRN BY. | CHKD. | APPD. | STATUS
USED ON | C UOB-HEP 20 15

UNIVERSITY OF BRISTOL
HIGH ENERGY PHYSICS GROUP
TITLE
MODULE: ltm9007_input_filter_v2

H.H.WILLS PHYSICS LAB, TYNDALL AVE, BRISTOL, BS8 1TL.

TOTAL NO. OF SHEETS

Fri Apr 21 10:51:28 | 2017

D. CUSSANS

ISSUE | DATE | MOD NO. | DRN BY. | CHKD. | APPD. | STATUS
USED ON | C UOB-HEP 20 15

UNIVERSITY OF BRISTOL
HIGH ENERGY PHYSICS GROUP
TITLE
MODULE: ltm9007_input_filter_v2

H.H.WILLS PHYSICS LAB, TYNDALL AVE, BRISTOL, BS8 1TL.

TOTAL NO. OF SHEETS

Fri Apr 21 10:51:28 | 2017

D. CUSSANS

ISSUE | DATE | MOD NO. | DRN BY. | CHKD. | APPD. | STATUS
USED ON | C UOB-HEP 20 15

UNIVERSITY OF BRISTOL
HIGH ENERGY PHYSICS GROUP
TITLE
MODULE: ltm9007_input_filter_v2

H.H.WILLS PHYSICS LAB, TYNDALL AVE, BRISTOL, BS8 1TL.

TOTAL NO. OF SHEETS

Fri Apr 21 10:51:28 | 2017

D. CUSSANS

ISSUE | DATE | MOD NO. | DRN BY. | CHKD. | APPD. | STATUS
USED ON | C UOB-HEP 20 15

UNIVERSITY OF BRISTOL
HIGH ENERGY PHYSICS GROUP
TITLE
MODULE: ltm9007_input_filter_v2

H.H.WILLS PHYSICS LAB, TYNDALL AVE, BRISTOL, BS8 1TL.

TOTAL NO. OF SHEETS

Fri Apr 21 10:51:28 | 2017

D. CUSSANS

ISSUE | DATE | MOD NO. | DRN BY. | CHKD. | APPD. | STATUS
USED ON | C UOB-HEP 20 15

UNIVERSITY OF BRISTOL
HIGH ENERGY PHYSICS GROUP
TITLE
MODULE: ltm9007_input_filter_v2

H.H.WILLS PHYSICS LAB, TYNDALL AVE, BRISTOL, BS8 1TL.

TOTAL NO. OF SHEETS

Fri Apr 21 10:51:28 | 2017

D. CUSSANS

ISSUE | DATE | MOD NO. | DRN BY. | CHKD. | APPD. | STATUS
USED ON | C UOB-HEP 20 15

UNIVERSITY OF BRISTOL
HIGH ENERGY PHYSICS GROUP
TITLE
MODULE: ltm9007_input_filter_v2

H.H.WILLS PHYSICS LAB, TYNDALL AVE, BRISTOL, BS8 1TL.

TOTAL NO. OF SHEETS

IN CSB M5 | J10 J9 | 100
IN | R23_3 1%

Fri Apr 21 10:51:29 | 2017

D. CUSSANS

ISSUE | DATE | MOD NO. | DRN BY. | CHKD. | APPD. | STATUS

H.H.WILLS PHYSICS LAB, TYNDALL AVE, BRISTOL, BS8 1TL.

TOTAL NO. OF SHEETS

AFILT+ AIN- AIN+

Fri Apr 21 10:51:29 | 2017

D. CUSSANS

ISSUE | DATE | MOD NO. | DRN BY. | CHKD. | APPD. | STATUS
USED ON | C UOB-HEP 20 15

UNIVERSITY OF BRISTOL
HIGH ENERGY PHYSICS GROUP
TITLE
MODULE: ltm9007_8chan_v2

H.H.WILLS PHYSICS LAB, TYNDALL AVE, BRISTOL, BS8 1TL.

TOTAL NO. OF SHEETS

FILTER; FOR ADC INPUTS; OVERALL PAGE:; MODULE PAGE:; uob_hep_pc051a_lib; AIN-; AFILT+ AFILT- AIN+; OUT; UOB-HEP

Fri Apr 21 10:51:28 | 2017

D. CUSSANS

ISSUE | DATE | MOD NO. | DRN BY. | CHKD. | APPD. | STATUS
USED ON | C UOB-HEP 20 15

UNIVERSITY OF BRISTOL
HIGH ENERGY PHYSICS GROUP
TITLE
MODULE: ltm9007_input_filter_v2

H.H.WILLS PHYSICS LAB, TYNDALL AVE, BRISTOL, BS8 1TL.

TOTAL NO. OF SHEETS

Fri Apr 21 10:51:28 | 2017

D. CUSSANS

ISSUE | DATE | MOD NO. | DRN BY. | CHKD. | APPD. | STATUS
USED ON | C UOB-HEP 20 15

UNIVERSITY OF BRISTOL
HIGH ENERGY PHYSICS GROUP
TITLE
MODULE: ltm9007_input_filter_v2

H.H.WILLS PHYSICS LAB, TYNDALL AVE, BRISTOL, BS8 1TL.

TOTAL NO. OF SHEETS

Fri Apr 21 10:51:28 | 2017

D. CUSSANS

ISSUE | DATE | MOD NO. | DRN BY. | CHKD. | APPD. | STATUS
USED ON | C UOB-HEP 20 15

UNIVERSITY OF BRISTOL
HIGH ENERGY PHYSICS GROUP
TITLE
MODULE: ltm9007_input_filter_v2

H.H.WILLS PHYSICS LAB, TYNDALL AVE, BRISTOL, BS8 1TL.

TOTAL NO. OF SHEETS

Fri Apr 21 10:51:28 | 2017

D. CUSSANS

ISSUE | DATE | MOD NO. | DRN BY. | CHKD. | APPD. | STATUS
USED ON | C UOB-HEP 20 15

UNIVERSITY OF BRISTOL
HIGH ENERGY PHYSICS GROUP
TITLE
MODULE: ltm9007_input_filter_v2

H.H.WILLS PHYSICS LAB, TYNDALL AVE, BRISTOL, BS8 1TL.

TOTAL NO. OF SHEETS

Fri Apr 21 10:51:28 | 2017

D. CUSSANS

ISSUE | DATE | MOD NO. | DRN BY. | CHKD. | APPD. | STATUS
USED ON | C UOB-HEP 20 15

UNIVERSITY OF BRISTOL
HIGH ENERGY PHYSICS GROUP
TITLE
MODULE: ltm9007_input_filter_v2

H.H.WILLS PHYSICS LAB, TYNDALL AVE, BRISTOL, BS8 1TL.

TOTAL NO. OF SHEETS

Fri Apr 21 10:51:28 | 2017

D. CUSSANS

ISSUE | DATE | MOD NO. | DRN BY. | CHKD. | APPD. | STATUS
USED ON | C UOB-HEP 20 15

UNIVERSITY OF BRISTOL
HIGH ENERGY PHYSICS GROUP
TITLE
MODULE: ltm9007_input_filter_v2

H.H.WILLS PHYSICS LAB, TYNDALL AVE, BRISTOL, BS8 1TL.

TOTAL NO. OF SHEETS

Fri Apr 21 10:51:28 | 2017

D. CUSSANS

ISSUE | DATE | MOD NO. | DRN BY. | CHKD. | APPD. | STATUS
USED ON | C UOB-HEP 20 15

UNIVERSITY OF BRISTOL
HIGH ENERGY PHYSICS GROUP
TITLE
MODULE: ltm9007_input_filter_v2

H.H.WILLS PHYSICS LAB, TYNDALL AVE, BRISTOL, BS8 1TL.

TOTAL NO. OF SHEETS

Fri Apr 21 10:51:28 | 2017

D. CUSSANS

ISSUE | DATE | MOD NO. | DRN BY. | CHKD. | APPD. | STATUS
USED ON | C UOB-HEP 20 15

UNIVERSITY OF BRISTOL
HIGH ENERGY PHYSICS GROUP
TITLE
MODULE: ltm9007_input_filter_v2

H.H.WILLS PHYSICS LAB, TYNDALL AVE, BRISTOL, BS8 1TL.

TOTAL NO. OF SHEETS

IN CSB M5 | J10 J9 | 100
IN | R23_4 1%

Fri Apr 21 10:51:29 | 2017

D. CUSSANS

ISSUE | DATE | MOD NO. | DRN BY. | CHKD. | APPD. | STATUS

H.H.WILLS PHYSICS LAB, TYNDALL AVE, BRISTOL, BS8 1TL.

TOTAL NO. OF SHEETS

AFILT+ AIN- AIN+

Fri Apr 21 10:51:29 | 2017

D. CUSSANS

ISSUE | DATE | MOD NO. | DRN BY. | CHKD. | APPD. | STATUS
USED ON | C UOB-HEP 20 15

UNIVERSITY OF BRISTOL
HIGH ENERGY PHYSICS GROUP
TITLE
MODULE: ltm9007_8chan_v2

H.H.WILLS PHYSICS LAB, TYNDALL AVE, BRISTOL, BS8 1TL.

TOTAL NO. OF SHEETS

Fri Apr 21 10:51:28 | 2017

D. CUSSANS

ISSUE | DATE | MOD NO. | DRN BY. | CHKD. | APPD. | STATUS
USED ON | C UOB-HEP 20 15

UNIVERSITY OF BRISTOL
HIGH ENERGY PHYSICS GROUP
TITLE
MODULE: ltm9007_input_filter_v2

H.H.WILLS PHYSICS LAB, TYNDALL AVE, BRISTOL, BS8 1TL.

TOTAL NO. OF SHEETS

FILTER; FOR ADC INPUTS; OVERALL PAGE:; MODULE PAGE:; uob_hep_pc051a_lib; AIN-; AFILT+ AFILT- AIN+; OUT; UOB-HEP

Fri Apr 21 10:51:28 | 2017

D. CUSSANS

ISSUE | DATE | MOD NO. | DRN BY. | CHKD. | APPD. | STATUS
USED ON | C UOB-HEP 20 15

UNIVERSITY OF BRISTOL
HIGH ENERGY PHYSICS GROUP
TITLE
MODULE: ltm9007_input_filter_v2

H.H.WILLS PHYSICS LAB, TYNDALL AVE, BRISTOL, BS8 1TL.

TOTAL NO. OF SHEETS

Fri Apr 21 10:51:28 | 2017

D. CUSSANS

ISSUE | DATE | MOD NO. | DRN BY. | CHKD. | APPD. | STATUS
USED ON | C UOB-HEP 20 15

UNIVERSITY OF BRISTOL
HIGH ENERGY PHYSICS GROUP
TITLE
MODULE: ltm9007_input_filter_v2

H.H.WILLS PHYSICS LAB, TYNDALL AVE, BRISTOL, BS8 1TL.

TOTAL NO. OF SHEETS

Fri Apr 21 10:51:28 | 2017

D. CUSSANS

ISSUE | DATE | MOD NO. | DRN BY. | CHKD. | APPD. | STATUS
USED ON | C UOB-HEP 20 15

UNIVERSITY OF BRISTOL
HIGH ENERGY PHYSICS GROUP
TITLE
MODULE: ltm9007_input_filter_v2

H.H.WILLS PHYSICS LAB, TYNDALL AVE, BRISTOL, BS8 1TL.

TOTAL NO. OF SHEETS

Fri Apr 21 10:51:28 | 2017

D. CUSSANS

ISSUE | DATE | MOD NO. | DRN BY. | CHKD. | APPD. | STATUS
USED ON | C UOB-HEP 20 15

UNIVERSITY OF BRISTOL
HIGH ENERGY PHYSICS GROUP
TITLE
MODULE: ltm9007_input_filter_v2

H.H.WILLS PHYSICS LAB, TYNDALL AVE, BRISTOL, BS8 1TL.

TOTAL NO. OF SHEETS

Fri Apr 21 10:51:28 | 2017

D. CUSSANS

ISSUE | DATE | MOD NO. | DRN BY. | CHKD. | APPD. | STATUS
USED ON | C UOB-HEP 20 15

UNIVERSITY OF BRISTOL
HIGH ENERGY PHYSICS GROUP
TITLE
MODULE: ltm9007_input_filter_v2

H.H.WILLS PHYSICS LAB, TYNDALL AVE, BRISTOL, BS8 1TL.

TOTAL NO. OF SHEETS

Fri Apr 21 10:51:28 | 2017

D. CUSSANS

ISSUE | DATE | MOD NO. | DRN BY. | CHKD. | APPD. | STATUS
USED ON | C UOB-HEP 20 15

UNIVERSITY OF BRISTOL
HIGH ENERGY PHYSICS GROUP
TITLE
MODULE: ltm9007_input_filter_v2

H.H.WILLS PHYSICS LAB, TYNDALL AVE, BRISTOL, BS8 1TL.

TOTAL NO. OF SHEETS

Fri Apr 21 10:51:28 | 2017

D. CUSSANS

ISSUE | DATE | MOD NO. | DRN BY. | CHKD. | APPD. | STATUS
USED ON | C UOB-HEP 20 15

UNIVERSITY OF BRISTOL
HIGH ENERGY PHYSICS GROUP
TITLE
MODULE: ltm9007_input_filter_v2

H.H.WILLS PHYSICS LAB, TYNDALL AVE, BRISTOL, BS8 1TL.

TOTAL NO. OF SHEETS

IN CSB M5 | J10 J9 | 100
IN | R23_6 1%

Fri Apr 21 10:51:29 | 2017

D. CUSSANS

ISSUE | DATE | MOD NO. | DRN BY. | CHKD. | APPD. | STATUS

H.H.WILLS PHYSICS LAB, TYNDALL AVE, BRISTOL, BS8 1TL.

TOTAL NO. OF SHEETS

AFILT+ AIN- AIN+

Fri Apr 21 10:51:29 | 2017

D. CUSSANS

ISSUE | DATE | MOD NO. | DRN BY. | CHKD. | APPD. | STATUS
USED ON | C UOB-HEP 20 15

UNIVERSITY OF BRISTOL
HIGH ENERGY PHYSICS GROUP
TITLE
MODULE: ltm9007_8chan_v2

H.H.WILLS PHYSICS LAB, TYNDALL AVE, BRISTOL, BS8 1TL.

TOTAL NO. OF SHEETS

Fri Apr 21 10:51:28 | 2017

D. CUSSANS

ISSUE | DATE | MOD NO. | DRN BY. | CHKD. | APPD. | STATUS
USED ON | C UOB-HEP 20 15

UNIVERSITY OF BRISTOL
HIGH ENERGY PHYSICS GROUP
TITLE
MODULE: ltm9007_input_filter_v2

H.H.WILLS PHYSICS LAB, TYNDALL AVE, BRISTOL, BS8 1TL.

TOTAL NO. OF SHEETS

FILTER; FOR ADC INPUTS; OVERALL PAGE:; MODULE PAGE:; uob_hep_pc051a_lib; AIN-; AFILT+ AFILT- AIN+; OUT; UOB-HEP

Fri Apr 21 10:51:28 | 2017

D. CUSSANS

ISSUE | DATE | MOD NO. | DRN BY. | CHKD. | APPD. | STATUS
USED ON | C UOB-HEP 20 15

UNIVERSITY OF BRISTOL
HIGH ENERGY PHYSICS GROUP
TITLE
MODULE: ltm9007_input_filter_v2

H.H.WILLS PHYSICS LAB, TYNDALL AVE, BRISTOL, BS8 1TL.

TOTAL NO. OF SHEETS

Fri Apr 21 10:51:28 | 2017

D. CUSSANS

ISSUE | DATE | MOD NO. | DRN BY. | CHKD. | APPD. | STATUS
USED ON | C UOB-HEP 20 15

UNIVERSITY OF BRISTOL
HIGH ENERGY PHYSICS GROUP
TITLE
MODULE: ltm9007_input_filter_v2

H.H.WILLS PHYSICS LAB, TYNDALL AVE, BRISTOL, BS8 1TL.

TOTAL NO. OF SHEETS

Fri Apr 21 10:51:28 | 2017

D. CUSSANS

ISSUE | DATE | MOD NO. | DRN BY. | CHKD. | APPD. | STATUS
USED ON | C UOB-HEP 20 15

UNIVERSITY OF BRISTOL
HIGH ENERGY PHYSICS GROUP
TITLE
MODULE: ltm9007_input_filter_v2

H.H.WILLS PHYSICS LAB, TYNDALL AVE, BRISTOL, BS8 1TL.

TOTAL NO. OF SHEETS

Fri Apr 21 10:51:28 | 2017

D. CUSSANS

ISSUE | DATE | MOD NO. | DRN BY. | CHKD. | APPD. | STATUS
USED ON | C UOB-HEP 20 15

UNIVERSITY OF BRISTOL
HIGH ENERGY PHYSICS GROUP
TITLE
MODULE: ltm9007_input_filter_v2

H.H.WILLS PHYSICS LAB, TYNDALL AVE, BRISTOL, BS8 1TL.

TOTAL NO. OF SHEETS

Fri Apr 21 10:51:28 | 2017

D. CUSSANS

ISSUE | DATE | MOD NO. | DRN BY. | CHKD. | APPD. | STATUS
USED ON | C UOB-HEP 20 15

UNIVERSITY OF BRISTOL
HIGH ENERGY PHYSICS GROUP
TITLE
MODULE: ltm9007_input_filter_v2

H.H.WILLS PHYSICS LAB, TYNDALL AVE, BRISTOL, BS8 1TL.

TOTAL NO. OF SHEETS

Fri Apr 21 10:51:28 | 2017

D. CUSSANS

ISSUE | DATE | MOD NO. | DRN BY. | CHKD. | APPD. | STATUS
USED ON | C UOB-HEP 20 15

UNIVERSITY OF BRISTOL
HIGH ENERGY PHYSICS GROUP
TITLE
MODULE: ltm9007_input_filter_v2

H.H.WILLS PHYSICS LAB, TYNDALL AVE, BRISTOL, BS8 1TL.

TOTAL NO. OF SHEETS

Fri Apr 21 10:51:28 | 2017

D. CUSSANS

ISSUE | DATE | MOD NO. | DRN BY. | CHKD. | APPD. | STATUS
USED ON | C UOB-HEP 20 15

UNIVERSITY OF BRISTOL
HIGH ENERGY PHYSICS GROUP
TITLE
MODULE: ltm9007_input_filter_v2

H.H.WILLS PHYSICS LAB, TYNDALL AVE, BRISTOL, BS8 1TL.

TOTAL NO. OF SHEETS

IN CSB M5 | J10 J9 | 100
IN | R23_7 1%

Fri Apr 21 10:51:29 | 2017

D. CUSSANS

ISSUE | DATE | MOD NO. | DRN BY. | CHKD. | APPD. | STATUS

H.H.WILLS PHYSICS LAB, TYNDALL AVE, BRISTOL, BS8 1TL.

TOTAL NO. OF SHEETS

AFILT+ AIN- AIN+

Fri Apr 21 10:51:29 | 2017

D. CUSSANS

ISSUE | DATE | MOD NO. | DRN BY. | CHKD. | APPD. | STATUS
USED ON | C UOB-HEP 20 15

UNIVERSITY OF BRISTOL
HIGH ENERGY PHYSICS GROUP
TITLE
MODULE: ltm9007_8chan_v2

H.H.WILLS PHYSICS LAB, TYNDALL AVE, BRISTOL, BS8 1TL.

TOTAL NO. OF SHEETS

Fri Apr 21 10:51:28 | 2017

D. CUSSANS

ISSUE | DATE | MOD NO. | DRN BY. | CHKD. | APPD. | STATUS
USED ON | C UOB-HEP 20 15

UNIVERSITY OF BRISTOL
HIGH ENERGY PHYSICS GROUP
TITLE
MODULE: ltm9007_input_filter_v2

H.H.WILLS PHYSICS LAB, TYNDALL AVE, BRISTOL, BS8 1TL.

TOTAL NO. OF SHEETS

Fri Apr 21 10:51:28 | 2017

D. CUSSANS

ISSUE | DATE | MOD NO. | DRN BY. | CHKD. | APPD. | STATUS
USED ON | C UOB-HEP 20 15

UNIVERSITY OF BRISTOL
HIGH ENERGY PHYSICS GROUP
TITLE
MODULE: ltm9007_input_filter_v2

H.H.WILLS PHYSICS LAB, TYNDALL AVE, BRISTOL, BS8 1TL.

TOTAL NO. OF SHEETS

FILTER; FOR ADC INPUTS; OVERALL PAGE:; MODULE PAGE:; uob_hep_pc051a_lib; AIN-; AFILT+ AFILT- AIN+; OUT; UOB-HEP

Fri Apr 21 10:51:28 | 2017

D. CUSSANS

ISSUE | DATE | MOD NO. | DRN BY. | CHKD. | APPD. | STATUS
USED ON | C UOB-HEP 20 15

UNIVERSITY OF BRISTOL
HIGH ENERGY PHYSICS GROUP
TITLE
MODULE: ltm9007_input_filter_v2

H.H.WILLS PHYSICS LAB, TYNDALL AVE, BRISTOL, BS8 1TL.

TOTAL NO. OF SHEETS

Fri Apr 21 10:51:28 | 2017

D. CUSSANS

ISSUE | DATE | MOD NO. | DRN BY. | CHKD. | APPD. | STATUS
USED ON | C UOB-HEP 20 15

UNIVERSITY OF BRISTOL
HIGH ENERGY PHYSICS GROUP
TITLE
MODULE: ltm9007_input_filter_v2

H.H.WILLS PHYSICS LAB, TYNDALL AVE, BRISTOL, BS8 1TL.

TOTAL NO. OF SHEETS

Fri Apr 21 10:51:28 | 2017

D. CUSSANS

ISSUE | DATE | MOD NO. | DRN BY. | CHKD. | APPD. | STATUS
USED ON | C UOB-HEP 20 15

UNIVERSITY OF BRISTOL
HIGH ENERGY PHYSICS GROUP
TITLE
MODULE: ltm9007_input_filter_v2

H.H.WILLS PHYSICS LAB, TYNDALL AVE, BRISTOL, BS8 1TL.

TOTAL NO. OF SHEETS

Fri Apr 21 10:51:28 | 2017

D. CUSSANS

ISSUE | DATE | MOD NO. | DRN BY. | CHKD. | APPD. | STATUS
USED ON | C UOB-HEP 20 15

UNIVERSITY OF BRISTOL
HIGH ENERGY PHYSICS GROUP
TITLE
MODULE: ltm9007_input_filter_v2

H.H.WILLS PHYSICS LAB, TYNDALL AVE, BRISTOL, BS8 1TL.

TOTAL NO. OF SHEETS

Fri Apr 21 10:51:28 | 2017

D. CUSSANS

ISSUE | DATE | MOD NO. | DRN BY. | CHKD. | APPD. | STATUS
USED ON | C UOB-HEP 20 15

UNIVERSITY OF BRISTOL
HIGH ENERGY PHYSICS GROUP
TITLE
MODULE: ltm9007_input_filter_v2

H.H.WILLS PHYSICS LAB, TYNDALL AVE, BRISTOL, BS8 1TL.

TOTAL NO. OF SHEETS

Fri Apr 21 10:51:28 | 2017

D. CUSSANS

ISSUE | DATE | MOD NO. | DRN BY. | CHKD. | APPD. | STATUS
USED ON | C UOB-HEP 20 15

UNIVERSITY OF BRISTOL
HIGH ENERGY PHYSICS GROUP
TITLE
MODULE: ltm9007_input_filter_v2

H.H.WILLS PHYSICS LAB, TYNDALL AVE, BRISTOL, BS8 1TL.

TOTAL NO. OF SHEETS

IN CSB M5 | J10 J9 | 100
IN | R23_8 1%

Fri Apr 21 10:51:29 | 2017

D. CUSSANS

ISSUE | DATE | MOD NO. | DRN BY. | CHKD. | APPD. | STATUS

H.H.WILLS PHYSICS LAB, TYNDALL AVE, BRISTOL, BS8 1TL.

TOTAL NO. OF SHEETS

AFILT+ AIN- AIN+

Fri Apr 21 10:51:29 | 2017

D. CUSSANS

ISSUE | DATE | MOD NO. | DRN BY. | CHKD. | APPD. | STATUS
USED ON | C UOB-HEP 20 15

UNIVERSITY OF BRISTOL
HIGH ENERGY PHYSICS GROUP
TITLE
MODULE: ltm9007_8chan_v2

H.H.WILLS PHYSICS LAB, TYNDALL AVE, BRISTOL, BS8 1TL.

TOTAL NO. OF SHEETS

Fri Apr 21 10:51:28 | 2017

D. CUSSANS

ISSUE | DATE | MOD NO. | DRN BY. | CHKD. | APPD. | STATUS
USED ON | C UOB-HEP 20 15

UNIVERSITY OF BRISTOL
HIGH ENERGY PHYSICS GROUP
TITLE
MODULE: ltm9007_input_filter_v2

H.H.WILLS PHYSICS LAB, TYNDALL AVE, BRISTOL, BS8 1TL.

TOTAL NO. OF SHEETS

Fri Apr 21 10:51:28 | 2017

D. CUSSANS

ISSUE | DATE | MOD NO. | DRN BY. | CHKD. | APPD. | STATUS
USED ON | C UOB-HEP 20 15

UNIVERSITY OF BRISTOL
HIGH ENERGY PHYSICS GROUP
TITLE
MODULE: ltm9007_input_filter_v2

H.H.WILLS PHYSICS LAB, TYNDALL AVE, BRISTOL, BS8 1TL.

TOTAL NO. OF SHEETS

FILTER; FOR ADC INPUTS; OVERALL PAGE:; MODULE PAGE:; uob_hep_pc051a_lib; AIN-; AFILT+ AFILT- AIN+; OUT; UOB-HEP

Fri Apr 21 10:51:28 | 2017

D. CUSSANS

ISSUE | DATE | MOD NO. | DRN BY. | CHKD. | APPD. | STATUS
USED ON | C UOB-HEP 20 15

UNIVERSITY OF BRISTOL
HIGH ENERGY PHYSICS GROUP
TITLE
MODULE: ltm9007_input_filter_v2

H.H.WILLS PHYSICS LAB, TYNDALL AVE, BRISTOL, BS8 1TL.

TOTAL NO. OF SHEETS

Fri Apr 21 10:51:28 | 2017

D. CUSSANS

ISSUE | DATE | MOD NO. | DRN BY. | CHKD. | APPD. | STATUS
USED ON | C UOB-HEP 20 15

UNIVERSITY OF BRISTOL
HIGH ENERGY PHYSICS GROUP
TITLE
MODULE: ltm9007_input_filter_v2

H.H.WILLS PHYSICS LAB, TYNDALL AVE, BRISTOL, BS8 1TL.

TOTAL NO. OF SHEETS

Fri Apr 21 10:51:28 | 2017

D. CUSSANS

ISSUE | DATE | MOD NO. | DRN BY. | CHKD. | APPD. | STATUS
USED ON | C UOB-HEP 20 15

UNIVERSITY OF BRISTOL
HIGH ENERGY PHYSICS GROUP
TITLE
MODULE: ltm9007_input_filter_v2

H.H.WILLS PHYSICS LAB, TYNDALL AVE, BRISTOL, BS8 1TL.

TOTAL NO. OF SHEETS

Fri Apr 21 10:51:28 | 2017

D. CUSSANS

ISSUE | DATE | MOD NO. | DRN BY. | CHKD. | APPD. | STATUS
USED ON | C UOB-HEP 20 15

UNIVERSITY OF BRISTOL
HIGH ENERGY PHYSICS GROUP
TITLE
MODULE: ltm9007_input_filter_v2

H.H.WILLS PHYSICS LAB, TYNDALL AVE, BRISTOL, BS8 1TL.

TOTAL NO. OF SHEETS

Fri Apr 21 10:51:28 | 2017

D. CUSSANS

ISSUE | DATE | MOD NO. | DRN BY. | CHKD. | APPD. | STATUS
USED ON | C UOB-HEP 20 15

UNIVERSITY OF BRISTOL
HIGH ENERGY PHYSICS GROUP
TITLE
MODULE: ltm9007_input_filter_v2

H.H.WILLS PHYSICS LAB, TYNDALL AVE, BRISTOL, BS8 1TL.

TOTAL NO. OF SHEETS

Fri Apr 21 10:51:28 | 2017

D. CUSSANS

ISSUE | DATE | MOD NO. | DRN BY. | CHKD. | APPD. | STATUS
USED ON | C UOB-HEP 20 15

UNIVERSITY OF BRISTOL
HIGH ENERGY PHYSICS GROUP
TITLE
MODULE: ltm9007_input_filter_v2

H.H.WILLS PHYSICS LAB, TYNDALL AVE, BRISTOL, BS8 1TL.

TOTAL NO. OF SHEETS

IN CSB M5 | J10 J9 | 100
IN | R23_9 1%

Fri Apr 21 10:51:29 | 2017

D. CUSSANS

ISSUE | DATE | MOD NO. | DRN BY. | CHKD. | APPD. | STATUS

H.H.WILLS PHYSICS LAB, TYNDALL AVE, BRISTOL, BS8 1TL.

TOTAL NO. OF SHEETS

AFILT+ AIN- AIN+

Fri Apr 21 10:51:29 | 2017

D. CUSSANS

ISSUE | DATE | MOD NO. | DRN BY. | CHKD. | APPD. | STATUS
USED ON | C UOB-HEP 20 15

UNIVERSITY OF BRISTOL
HIGH ENERGY PHYSICS GROUP
TITLE
MODULE: ltm9007_8chan_v2

H.H.WILLS PHYSICS LAB, TYNDALL AVE, BRISTOL, BS8 1TL.

TOTAL NO. OF SHEETS

Fri Apr 21 10:51:28 | 2017

D. CUSSANS

ISSUE | DATE | MOD NO. | DRN BY. | CHKD. | APPD. | STATUS
USED ON | C UOB-HEP 20 15

UNIVERSITY OF BRISTOL
HIGH ENERGY PHYSICS GROUP
TITLE
MODULE: ltm9007_input_filter_v2

H.H.WILLS PHYSICS LAB, TYNDALL AVE, BRISTOL, BS8 1TL.

TOTAL NO. OF SHEETS

Fri Apr 21 10:51:28 | 2017

D. CUSSANS

ISSUE | DATE | MOD NO. | DRN BY. | CHKD. | APPD. | STATUS
USED ON | C UOB-HEP 20 15

UNIVERSITY OF BRISTOL
HIGH ENERGY PHYSICS GROUP
TITLE
MODULE: ltm9007_input_filter_v2

H.H.WILLS PHYSICS LAB, TYNDALL AVE, BRISTOL, BS8 1TL.

TOTAL NO. OF SHEETS

FILTER; FOR ADC INPUTS; OVERALL PAGE:; MODULE PAGE:; uob_hep_pc051a_lib; AIN-; AFILT+ AFILT- AIN+; OUT; UOB-HEP

Fri Apr 21 10:51:28 | 2017

D. CUSSANS

ISSUE | DATE | MOD NO. | DRN BY. | CHKD. | APPD. | STATUS
USED ON | C UOB-HEP 20 15

UNIVERSITY OF BRISTOL
HIGH ENERGY PHYSICS GROUP
TITLE
MODULE: ltm9007_input_filter_v2

H.H.WILLS PHYSICS LAB, TYNDALL AVE, BRISTOL, BS8 1TL.

TOTAL NO. OF SHEETS

Fri Apr 21 10:51:28 | 2017

D. CUSSANS

ISSUE | DATE | MOD NO. | DRN BY. | CHKD. | APPD. | STATUS
USED ON | C UOB-HEP 20 15

UNIVERSITY OF BRISTOL
HIGH ENERGY PHYSICS GROUP
TITLE
MODULE: ltm9007_input_filter_v2

H.H.WILLS PHYSICS LAB, TYNDALL AVE, BRISTOL, BS8 1TL.

TOTAL NO. OF SHEETS

Fri Apr 21 10:51:28 | 2017

D. CUSSANS

ISSUE | DATE | MOD NO. | DRN BY. | CHKD. | APPD. | STATUS
USED ON | C UOB-HEP 20 15

UNIVERSITY OF BRISTOL
HIGH ENERGY PHYSICS GROUP
TITLE
MODULE: ltm9007_input_filter_v2

H.H.WILLS PHYSICS LAB, TYNDALL AVE, BRISTOL, BS8 1TL.

TOTAL NO. OF SHEETS

Fri Apr 21 10:51:28 | 2017

D. CUSSANS

ISSUE | DATE | MOD NO. | DRN BY. | CHKD. | APPD. | STATUS
USED ON | C UOB-HEP 20 15

UNIVERSITY OF BRISTOL
HIGH ENERGY PHYSICS GROUP
TITLE
MODULE: ltm9007_input_filter_v2

H.H.WILLS PHYSICS LAB, TYNDALL AVE, BRISTOL, BS8 1TL.

TOTAL NO. OF SHEETS

Fri Apr 21 10:51:28 | 2017

D. CUSSANS

ISSUE | DATE | MOD NO. | DRN BY. | CHKD. | APPD. | STATUS
USED ON | C UOB-HEP 20 15

UNIVERSITY OF BRISTOL
HIGH ENERGY PHYSICS GROUP
TITLE
MODULE: ltm9007_input_filter_v2

H.H.WILLS PHYSICS LAB, TYNDALL AVE, BRISTOL, BS8 1TL.

TOTAL NO. OF SHEETS

Fri Apr 21 10:51:28 | 2017

D. CUSSANS

ISSUE | DATE | MOD NO. | DRN BY. | CHKD. | APPD. | STATUS
USED ON | C UOB-HEP 20 15

UNIVERSITY OF BRISTOL
HIGH ENERGY PHYSICS GROUP
TITLE
MODULE: ltm9007_input_filter_v2

H.H.WILLS PHYSICS LAB, TYNDALL AVE, BRISTOL, BS8 1TL.

TOTAL NO. OF SHEETS

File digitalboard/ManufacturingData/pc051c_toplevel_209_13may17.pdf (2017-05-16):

## POWER REGULATION

## 8 X LTM9007

PAGE 15; FPGA; ( TRENZ TE0712; PAGE 14; PAGE 13; JTAG; PAGE 12 PAGE 10; SFP CAGES; 4 X DIN 41612; PAGE 5; PAGE 6-9 PAGE 4 PAGE 2,3; LEDS ADC; OVERALL LAYOUT; PAGE 11; CLOCK GENERATION; ESATA CONNECTORS; CPLD; (MULTIPLEXES; I2C,SPI); ALSO,; TEMPERATURE MONITOR,; uob_hep_pc051a_lib; UOB-HEP

CONNECTION TO AMPLIFIER

IP SELECT SWITCHES

CONNECTIONS TO FPGA

Mon Jul | 11 19:23:10 2016

DAVID CUSSANS

ISSUE | DATE | MOD NO. | DRN BY. | CHKD. | APPD. | STATUS

USED ON | C UOB-HEP 20

POWER-ON-RESET & UNIQUE ID

H.H.WILLS PHYSICS LAB, TYNDALL AVE, BRISTOL, BS8 1TL.

UNIVERSITY OF BRISTOL
HIGH ENERGY PHYSICS GROUP
TITLE
MODULE: pc051c_toplevel

MODULE PAGE: 1 OF 15
OVERALL PAGE: 1 OF 99

TOTAL NO. OF SHEETS

FOUR LTM9007 ADCS ( WITH INPUT FILTERS; ) 1 OF 2 ( 8 ADC TOTAL ); uob_hep_pc051a_lib; CLK_N<8..0>\BASE; CLK_P<8..0>\BASE; OUT_P<63..0>\BASE; OUT_N<63..0>\BASE; ADC_SDI<7..0>\BASE; ADC_SDOB<7..0>\BASE; ADC_CSB<7..0>\BASE; ADC_CSA<7..0>\BASE; ANA_IN_P<63..0>\BASE ANA_IN_N<63..0>\BASE; ADC_SCK<7..0>\BASE; ADC_SDOA<7..0>\BASE; LTM9007_8CHAN_V2; ANA_IN+<8..1>; CLKIN+; ANA_IN-<8..1>; CLKIN-; CSA; CSB; SCK; SDI; SDOB; SDOA; OUT-<8..1>; OUT+<8..1>; OUT; UOB-HEP

Fri Apr 21 10:51:31 | 2017

D. CUSSANS

ISSUE | DATE | MOD NO. | DRN BY. | CHKD. | APPD. | STATUS

USED ON | C UOB-HEP 20

H.H.WILLS PHYSICS LAB, TYNDALL AVE, BRISTOL, BS8 1TL.

UNIVERSITY OF BRISTOL
HIGH ENERGY PHYSICS GROUP
TITLE
MODULE: pc051c_toplevel

MODULE PAGE: 2 OF 15
OVERALL PAGE: 2 OF 99

Fri Apr 21 10:51:31 | 2017

D. CUSSANS

ISSUE | DATE | MOD NO. | DRN BY. | CHKD. | APPD. | STATUS

USED ON | C UOB-HEP 20

H.H.WILLS PHYSICS LAB, TYNDALL AVE, BRISTOL, BS8 1TL.

UNIVERSITY OF BRISTOL
HIGH ENERGY PHYSICS GROUP
TITLE
MODULE: pc051c_toplevel

MODULE PAGE: 3 OF 15
OVERALL PAGE: 3 OF 99


LIGHT PIPES MOUNT ABOVE LEDS

IF TEMP_ALARM LED GOES HIGH - OVER TEMP TRIP

PUT LEDS AND SWITCHES ON BANK 14
WHICH HAS VCCIO=3.3V

ISSUE | DATE | MOD NO. | DRN BY. | CHKD. | APPD. | STATUS

USED ON | C UOB-HEP 20

H.H.WILLS PHYSICS LAB, TYNDALL AVE, BRISTOL, BS8 1TL.

LEDS , ROTARY SWITCH FOR IP SELECTION


WANT TO KEEP GROUND AND POWER-PLANE NOISE AWAY FROM ADCS
AND GROUND PLANE OF REST OF BOARD

AIM FOR VERY LOW CSR CAPS

ROUTE BETWEEN BNX002 AND
REGULATOR WITH 5MM WIDE TRACK

ISSUE | DATE | MOD NO. | DRN BY. | CHKD. | APPD. | STATUS

USED ON | C UOB-HEP 20

H.H.WILLS PHYSICS LAB, TYNDALL AVE, BRISTOL, BS8 1TL.


BECAUSE OF THIN TRACK
CARRYING P3V3 TO DIN CONNECTORS
PUT DECOUPLING CLOSE TO I2C PULL-UPS
DO NOT DRAW MORE THAN 200MA PER CONNECTOR
( 800MA TOTAL ) ON P3V3

CONNECTOR FOR CABLE TO PCB
WITH CONNECTOR TO FRAME
FOR I2C TEMPERATURE MONITORING
OF SIPM

Sat May 13 20:53:12 | 2017

ISSUE | DATE | MOD NO. | DRN BY. | CHKD. | APPD. | STATUS

GPIO<8> IS FOR DEBUGGING

USED ON | C UOB-HEP 20

H.H.WILLS PHYSICS LAB, TYNDALL AVE, BRISTOL, BS8 1TL.

UNIVERSITY OF BRISTOL
HIGH ENERGY PHYSICS GROUP
TITLE
MODULE: pc051c_toplevel


BECAUSE OF THIN TRACK
CARRYING P3V3 TO DIN CONNECTORS
PUT DECOUPLING CLOSE TO I2C PULL-UPS
DO NOT DRAW MORE THAN 200MA PER CONNECTOR
( 800MA TOTAL ) ON P3V3

ISSUE | DATE | MOD NO. | DRN BY. | CHKD. | APPD. | STATUS

USED ON | C UOB-HEP 20

H.H.WILLS PHYSICS LAB, TYNDALL AVE, BRISTOL, BS8 1TL.

09 03 196 6921UNIVERSITY OF BRISTOL HIGH ENERGY PHYSICS GROUP


BECAUSE OF THIN TRACK
CARRYING P3V3 TO DIN CONNECTORS
PUT DECOUPLING CLOSE TO I2C PULL-UPS
DO NOT DRAW MORE THAN 200MA PER CONNECTOR
( 800MA TOTAL ) ON P3V3

ISSUE | DATE | MOD NO. | DRN BY. | CHKD. | APPD. | STATUS

USED ON | C UOB-HEP 20

H.H.WILLS PHYSICS LAB, TYNDALL AVE, BRISTOL, BS8 1TL.

09 03 196 6921UNIVERSITY OF BRISTOL HIGH ENERGY PHYSICS GROUP

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

ISSUE | DATE | MOD NO. | DRN BY. | CHKD. | APPD. | STATUS

USED ON | C UOB-HEP 20

H.H.WILLS PHYSICS LAB, TYNDALL AVE, BRISTOL, BS8 1TL.


PINS 1-10 TOWARDS BEZEL USE WITH A TYCO SFP CAGE

MGT_RX_N<0> | 12 | 19 MGT_TX_N<0>

SFP_SCL<0> | 5

4 | | 8 SFP_LOS<0>

11 | 17
14 | 20

SFP POWER CONSUMPTION UP TO 1W

SFP CAGES IN TWO PARTS
SEPARATE FROM SFP CONNECTOR

MGT_RX_N<1> | 12 | 19 MGT_TX_N<1>

6 | 3 SFP1_TX_DISABLE

SFP_SCL<1> | 5
IN SFP_SDA<1> | 4 | 8 SFP_LOS<1> | OUT

10

ONE NORMAL CONNECTIONS (MASTER)
OTHER WITH RX/TX SWAPPED (SLAVE)

Sat May 13 20:53:11 | 2017

ISSUE | DATE | MOD NO. | DRN BY. | CHKD. | APPD. | STATUS

USED ON | C UOB-HEP 20

H.H.WILLS PHYSICS LAB, TYNDALL AVE, BRISTOL, BS8 1TL.

TWO SFP , TWO ESATA

CROSS-OVER MEANS
CAN PLUG MASTER INTO SLAVE
WITH NORMAL SATA CABLE


IC10 SOT23 SN65LVDT2DBV

CLK40_IN_N

DIRECTLY COUPLE SHELL OF HDMI
TO SIGNAL REFERENCE ( GROUND ) PLANE
USE FERRITE CORES ON HDMI CABLES TO

ISSUE | DATE | MOD NO. | DRN BY. | CHKD. | APPD. | STATUS

USED ON | C UOB-HEP 20

H.H.WILLS PHYSICS LAB, TYNDALL AVE, BRISTOL, BS8 1TL.


HDMI_TDO_P 4

IC13 1 2 DS90LV032ATM/NOPB R55 100 1%

DISABLE FRONT-PANEL JTAG
BEFORE USING ON-BOARD JTAG CONNECTOR

PUT LINK ON SW4 TO
TAKE EN LOW
TO DISABLE FRONT-PANEL JTAG

Sat May 13 20:53:13 | 2017

D. CUSSANS

USED ON | C UOB-HEP 20

5 | CPLD_TCK

H.H.WILLS PHYSICS LAB, TYNDALL AVE, BRISTOL, BS8 1TL.

USED AS A CLOCK INPUT; VCCIO:; BANK 14 = 3.3V; BANK 13,15,16; ( CAN USE LVDS DIFF_TERM; uob_hep_pc051a_lib; SPI_SDO_FROM_ADC\BASE; SPI_SCK_FROM_FPGA\BASE; I2C_SCL_FROM_FPGA\BASE; I2C_SDA_TO_FPGA\BASE; I2C_SDA_FROM_FPGA\BASE; SPI_CSN_FROM_FPGA\BASE; SPI_SDI_FROM_FPGA\BASE; BUSY_3V3 B14_N<24..1>; CLK_GEN_RST_3V3*\BASE; CLK_GEN_LOL*\BASE; FPGA_LED\BASE; SFP_LOS<1..0>\BASE B14_P<24..1>; IP_ADDRESS_SELECT<7..0>\BASE B14_N<24..1>; BUS_SELECT<4..0>\BASE; OUT_P<63..0>\BASE; OUT_N<63..0>\BASE; OUT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

ARRANGE ORDER OF
ADC DATA FOR BEST
PCB ROUTING

Sat May 13 20:53:15 | 2017

D. CUSSANS

ISSUE | DATE | MOD NO. | DRN BY. | CHKD. | APPD. | STATUS

USED ON | C UOB-HEP 20

H.H.WILLS PHYSICS LAB, TYNDALL AVE, BRISTOL, BS8 1TL.

UNIVERSITY OF BRISTOL
HIGH ENERGY PHYSICS GROUP
TITLE
MODULE: pc051c_toplevel

PUT TERMINATION
AS CLOSE AS POSSIBLE

MAPPING OF SIGNALS TO FPGA PINS

MODULE PAGE: 13 OF 15
OVERALL PAGE: 13 OF 99

MUST *NOT* SHUTDOWNWHEN PGOOD IS LOW

Sat May 13 20:53:13 | 2017

D. CUSSANS

ISSUE | DATE | MOD NO. | DRN BY. | CHKD. | APPD. | STATUS

USED ON | C UOB-HEP 20

H.H.WILLS PHYSICS LAB, TYNDALL AVE, BRISTOL, BS8 1TL.

CPLD THAT MULTIPLEXES I2C AND SPI BUSES
TEMPERATURE MONITOR , POWER-ON-RESET , UNIQUE ID

D. CUSSANS

ISSUE | DATE | MOD NO. | DRN BY. | CHKD. | APPD. | STATUS

USED ON | C UOB-HEP 20

H.H.WILLS PHYSICS LAB, TYNDALL AVE, BRISTOL, BS8 1TL.

LEVEL FOR POWER GOOD SIGNAL FROM TRENZ BOARD

TRENZ TE0712; FPGA MODULE; uob_hep_pc051a_lib; PGOOD; NOSEQ; MODE; JTAGEN; 3.3V_VIN; 1.8VOUT; 3.3V_CTREF; VIN; VCCIO16; ETH_TD*; ETH_TD; ETH_RD*; ETH_RD; VIN_1; VIN_2; VIN_3; VCCIO16_1; VCCIO16_2; VBAT_IN; GND_1; GND_2; GND_3; GND_4; GND_5; GND_6; GND_7; GND_8; GND_9; GND_10; GND_11; GND_12; GND_13; GND_14; GND_15; 3.3VIN_1; 3.3VIN_2; OUT; UOB-HEP

Mon Apr 24 12:04:11 | 2017

D. CUSSANS

ISSUE | DATE | MOD NO. | DRN BY. | CHKD. | APPD. | STATUS
USED ON | C UOB-HEP 20 15

H.H.WILLS PHYSICS LAB, TYNDALL AVE, BRISTOL, BS8 1TL.

UNIVERSITY OF BRISTOL
HIGH ENERGY PHYSICS GROUP
TITLE

MODULE: trenz_te0712
MOUNTING HOLES AND JM1 CONNECTOR FOR

MODULE PAGE: 1 OF 3
OVERALL PAGE: 16 OF 99

TRENZ TE0712; FPGA MODULE; uob_hep_pc051a_lib; VIN; VCCIO15; VCCIO13; 3.3VOUT; 1.5VOUT; TDO; TDI; RESIN VREF_JTAG TCK; TMS; TCK; RESIN; 3.3V_JTAG; VIN_4; VIN_3; VIN_2; VIN_1; VCCIO15_2; VCCIO15_1; VCCIO13_2; VCCIO13_1; GND_9; GND_8; GND_7; GND_6; GND_5; GND_4; GND_3; GND_2; GND_12; GND_11; GND_10; GND_1; GND; OUT; UOB-HEP

Fri Apr 21 10:51:30 | 2017

D. CUSSANS

ISSUE | DATE | MOD NO. | DRN BY. | CHKD. | APPD. | STATUS
USED ON | C UOB-HEP 20 15

H.H.WILLS PHYSICS LAB, TYNDALL AVE, BRISTOL, BS8 1TL.

UNIVERSITY OF BRISTOL
HIGH ENERGY PHYSICS GROUP
TITLE
MODULE: trenz_te0712
CONNECTOR JM2 FOR

MODULE PAGE: 2 OF 3
OVERALL PAGE: 17 OF 99

TRENZ TE0712; FPGA MODULE; uob_hep_pc051a_lib; MGT_CLK1_N MGT_CLK1; CLKIN2_N CLKIN2; MGT_RX<3..0>; MGT_RX_N<3..0>; MGT_TX<3..0>; MGT_TX_N<3..0>; MGT_TX3* MGT_TX3 MGT_RX3* MGT_RX3; MGT_TX2* MGT_TX2 MGT_RX2* MGT_RX2; MGT_TX1* MGT_TX1 MGT_RX1* MGT_RX1; MGT_TX0* MGT_TX0 MGT_RX0* MGT_RX0; MGT_CLK1* MGT_CLK1; CLKIN2* CLKIN2; GND1; GND2; GND3; GND4; GND5; GND6; GND7; GND8; GND9; GND10; GND11; GND12; GND13; GND14; OUT; UOB-HEP

Fri Apr 21 10:51:31 | 2017

D. CUSSANS

ISSUE | DATE | MOD NO. | DRN BY. | CHKD. | APPD. | STATUS
USED ON | C UOB-HEP 20 15

H.H.WILLS PHYSICS LAB, TYNDALL AVE, BRISTOL, BS8 1TL.

UNIVERSITY OF BRISTOL
HIGH ENERGY PHYSICS GROUP
TITLE
MODULE: trenz_te0712
CONNECTOR JM3 FOR

MODULE PAGE: 3 OF 3
OVERALL PAGE: 18 OF 99

VDDA_CLK40 , VDDO_CLK40 = 3.3V; CLOCK CHIP; CLOCK GENERATION -; LICENSED; UNDER THE TAPR OPEN HARDWARE LICENSE; (WWW.TAPR.ORG/OHL); VDD_CLK40; USING; LVPECL; OSCILLATOR; Fri; Apr 21 13:03:46; uob_hep_pc051a_lib; CLK9_N; CLK9_P; VDDO_CLK40\G; VDD_CLK40\G; VDDA_CLK40\G; VDD_OSC\G; CLK_IN_AC_P CLK_IN_AC_N; CLK_IN_N; CLK_IN_P; INTR* LOL*; SCL SDA; RST*; CLK_OUT_N<8..0>; CLK_OUT_P<8..0>; 16V_GEN 100NF; 16V_GEN; 10V_GEN; 10V_GEN 22UF_X7R; SIL254D; VDD=VDD_OSC;GND=GND_SIGNAL; 50MHZ; MX575ABB50M0000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

ADD APPROPRIATE RESISTORS TO GND

VDD=VDD_CLK40;VDDA=VDDA_CLK40;GND=GND_SIGNAL

ISSUE | DATE | MOD NO. | DRN BY. | CHKD. | APPD. | STATUS

USED ON | C UOB-HEP 20

H.H.WILLS PHYSICS LAB, TYNDALL AVE, BRISTOL, BS8 1TL.

UNIVERSITY OF BRISTOL
HIGH ENERGY PHYSICS GROUP
TITLE
MODULE: fmc_tlu_clock_gen

MAKE SURE INDUCTOR CAN COPE
WITH ~ 300MA

MODULE PAGE: 1 OF 1
OVERALL PAGE: 19 OF 99

Fri Apr 21 10:51:29 | 2017

D. CUSSANS

ISSUE | DATE | MOD NO. | DRN BY. | CHKD. | APPD. | STATUS
USED ON | C UOB-HEP 20 15

H.H.WILLS PHYSICS LAB, TYNDALL AVE, BRISTOL, BS8 1TL.

AFILT+ AIN- AIN+

Fri Apr 21 10:51:29 | 2017

D. CUSSANS

ISSUE | DATE | MOD NO. | DRN BY. | CHKD. | APPD. | STATUS
USED ON | C UOB-HEP 20 15

H.H.WILLS PHYSICS LAB, TYNDALL AVE, BRISTOL, BS8 1TL.

UNIVERSITY OF BRISTOL
HIGH ENERGY PHYSICS GROUP
TITLE
MODULE: ltm9007_8chan_v2

MODULE PAGE: 2 OF 2
OVERALL PAGE: 21 OF 99

FILTER; FOR ADC INPUTS; uob_hep_pc051a_lib; AIN-; AFILT+ AFILT- AIN+; C6_1 C5_1 OUT; OUT; UOB-HEP

Fri Apr 21 10:51:28 | 2017

D. CUSSANS

ISSUE | DATE | MOD NO. | DRN BY. | CHKD. | APPD. | STATUS
USED ON | C UOB-HEP 20 15

H.H.WILLS PHYSICS LAB, TYNDALL AVE, BRISTOL, BS8 1TL.

UNIVERSITY OF BRISTOL
HIGH ENERGY PHYSICS GROUP
TITLE
MODULE: ltm9007_input_filter_v2

MODULE PAGE: 1 OF 1
OVERALL PAGE: 22 OF 99

Fri Apr 21 10:51:28 | 2017

D. CUSSANS

ISSUE | DATE | MOD NO. | DRN BY. | CHKD. | APPD. | STATUS
USED ON | C UOB-HEP 20 15

H.H.WILLS PHYSICS LAB, TYNDALL AVE, BRISTOL, BS8 1TL.

UNIVERSITY OF BRISTOL
HIGH ENERGY PHYSICS GROUP
TITLE
MODULE: ltm9007_input_filter_v2

MODULE PAGE: 1 OF 1
OVERALL PAGE: 23 OF 99

Fri Apr 21 10:51:28 | 2017

D. CUSSANS

ISSUE | DATE | MOD NO. | DRN BY. | CHKD. | APPD. | STATUS
USED ON | C UOB-HEP 20 15

H.H.WILLS PHYSICS LAB, TYNDALL AVE, BRISTOL, BS8 1TL.

UNIVERSITY OF BRISTOL
HIGH ENERGY PHYSICS GROUP
TITLE
MODULE: ltm9007_input_filter_v2

MODULE PAGE: 1 OF 1
OVERALL PAGE: 24 OF 99

Fri Apr 21 10:51:28 | 2017

D. CUSSANS

ISSUE | DATE | MOD NO. | DRN BY. | CHKD. | APPD. | STATUS
USED ON | C UOB-HEP 20 15

H.H.WILLS PHYSICS LAB, TYNDALL AVE, BRISTOL, BS8 1TL.

UNIVERSITY OF BRISTOL
HIGH ENERGY PHYSICS GROUP
TITLE
MODULE: ltm9007_input_filter_v2

MODULE PAGE: 1 OF 1
OVERALL PAGE: 25 OF 99

Fri Apr 21 10:51:28 | 2017

D. CUSSANS

ISSUE | DATE | MOD NO. | DRN BY. | CHKD. | APPD. | STATUS
USED ON | C UOB-HEP 20 15

H.H.WILLS PHYSICS LAB, TYNDALL AVE, BRISTOL, BS8 1TL.

UNIVERSITY OF BRISTOL
HIGH ENERGY PHYSICS GROUP
TITLE
MODULE: ltm9007_input_filter_v2

MODULE PAGE: 1 OF 1
OVERALL PAGE: 26 OF 99

Fri Apr 21 10:51:28 | 2017

D. CUSSANS

ISSUE | DATE | MOD NO. | DRN BY. | CHKD. | APPD. | STATUS
USED ON | C UOB-HEP 20 15

H.H.WILLS PHYSICS LAB, TYNDALL AVE, BRISTOL, BS8 1TL.

UNIVERSITY OF BRISTOL
HIGH ENERGY PHYSICS GROUP
TITLE
MODULE: ltm9007_input_filter_v2

MODULE PAGE: 1 OF 1
OVERALL PAGE: 27 OF 99

Fri Apr 21 10:51:28 | 2017

D. CUSSANS

ISSUE | DATE | MOD NO. | DRN BY. | CHKD. | APPD. | STATUS
USED ON | C UOB-HEP 20 15

H.H.WILLS PHYSICS LAB, TYNDALL AVE, BRISTOL, BS8 1TL.

UNIVERSITY OF BRISTOL
HIGH ENERGY PHYSICS GROUP
TITLE
MODULE: ltm9007_input_filter_v2

MODULE PAGE: 1 OF 1
OVERALL PAGE: 28 OF 99

Fri Apr 21 10:51:28 | 2017

D. CUSSANS

ISSUE | DATE | MOD NO. | DRN BY. | CHKD. | APPD. | STATUS
USED ON | C UOB-HEP 20 15

H.H.WILLS PHYSICS LAB, TYNDALL AVE, BRISTOL, BS8 1TL.

UNIVERSITY OF BRISTOL
HIGH ENERGY PHYSICS GROUP
TITLE
MODULE: ltm9007_input_filter_v2

MODULE PAGE: 1 OF 1
OVERALL PAGE: 29 OF 99

Fri Apr 21 10:51:29 | 2017

D. CUSSANS

ISSUE | DATE | MOD NO. | DRN BY. | CHKD. | APPD. | STATUS
USED ON | C UOB-HEP 20 15

H.H.WILLS PHYSICS LAB, TYNDALL AVE, BRISTOL, BS8 1TL.

AFILT+ AIN- AIN+

Fri Apr 21 10:51:29 | 2017

D. CUSSANS

ISSUE | DATE | MOD NO. | DRN BY. | CHKD. | APPD. | STATUS
USED ON | C UOB-HEP 20 15

H.H.WILLS PHYSICS LAB, TYNDALL AVE, BRISTOL, BS8 1TL.

UNIVERSITY OF BRISTOL
HIGH ENERGY PHYSICS GROUP
TITLE
MODULE: ltm9007_8chan_v2

MODULE PAGE: 2 OF 2
OVERALL PAGE: 31 OF 99

FILTER; FOR ADC INPUTS; uob_hep_pc051a_lib; AIN-; AFILT+ AFILT- AIN+; C6_2 C5_2 OUT; OUT; UOB-HEP

Fri Apr 21 10:51:28 | 2017

D. CUSSANS

ISSUE | DATE | MOD NO. | DRN BY. | CHKD. | APPD. | STATUS
USED ON | C UOB-HEP 20 15

H.H.WILLS PHYSICS LAB, TYNDALL AVE, BRISTOL, BS8 1TL.

UNIVERSITY OF BRISTOL
HIGH ENERGY PHYSICS GROUP
TITLE
MODULE: ltm9007_input_filter_v2

MODULE PAGE: 1 OF 1
OVERALL PAGE: 32 OF 99

Fri Apr 21 10:51:28 | 2017

D. CUSSANS

ISSUE | DATE | MOD NO. | DRN BY. | CHKD. | APPD. | STATUS
USED ON | C UOB-HEP 20 15

H.H.WILLS PHYSICS LAB, TYNDALL AVE, BRISTOL, BS8 1TL.

UNIVERSITY OF BRISTOL
HIGH ENERGY PHYSICS GROUP
TITLE
MODULE: ltm9007_input_filter_v2

MODULE PAGE: 1 OF 1
OVERALL PAGE: 33 OF 99

Fri Apr 21 10:51:28 | 2017

D. CUSSANS

ISSUE | DATE | MOD NO. | DRN BY. | CHKD. | APPD. | STATUS
USED ON | C UOB-HEP 20 15

H.H.WILLS PHYSICS LAB, TYNDALL AVE, BRISTOL, BS8 1TL.

UNIVERSITY OF BRISTOL
HIGH ENERGY PHYSICS GROUP
TITLE
MODULE: ltm9007_input_filter_v2

MODULE PAGE: 1 OF 1
OVERALL PAGE: 34 OF 99

Fri Apr 21 10:51:28 | 2017

D. CUSSANS

ISSUE | DATE | MOD NO. | DRN BY. | CHKD. | APPD. | STATUS
USED ON | C UOB-HEP 20 15

H.H.WILLS PHYSICS LAB, TYNDALL AVE, BRISTOL, BS8 1TL.

UNIVERSITY OF BRISTOL
HIGH ENERGY PHYSICS GROUP
TITLE
MODULE: ltm9007_input_filter_v2

MODULE PAGE: 1 OF 1
OVERALL PAGE: 35 OF 99

Fri Apr 21 10:51:28 | 2017

D. CUSSANS

ISSUE | DATE | MOD NO. | DRN BY. | CHKD. | APPD. | STATUS
USED ON | C UOB-HEP 20 15

H.H.WILLS PHYSICS LAB, TYNDALL AVE, BRISTOL, BS8 1TL.

UNIVERSITY OF BRISTOL
HIGH ENERGY PHYSICS GROUP
TITLE
MODULE: ltm9007_input_filter_v2

MODULE PAGE: 1 OF 1
OVERALL PAGE: 36 OF 99

Fri Apr 21 10:51:28 | 2017

D. CUSSANS

ISSUE | DATE | MOD NO. | DRN BY. | CHKD. | APPD. | STATUS
USED ON | C UOB-HEP 20 15

H.H.WILLS PHYSICS LAB, TYNDALL AVE, BRISTOL, BS8 1TL.

UNIVERSITY OF BRISTOL
HIGH ENERGY PHYSICS GROUP
TITLE
MODULE: ltm9007_input_filter_v2

MODULE PAGE: 1 OF 1
OVERALL PAGE: 37 OF 99

Fri Apr 21 10:51:28 | 2017

D. CUSSANS

ISSUE | DATE | MOD NO. | DRN BY. | CHKD. | APPD. | STATUS
USED ON | C UOB-HEP 20 15

H.H.WILLS PHYSICS LAB, TYNDALL AVE, BRISTOL, BS8 1TL.

UNIVERSITY OF BRISTOL
HIGH ENERGY PHYSICS GROUP
TITLE
MODULE: ltm9007_input_filter_v2

MODULE PAGE: 1 OF 1
OVERALL PAGE: 38 OF 99

Fri Apr 21 10:51:28 | 2017

D. CUSSANS

ISSUE | DATE | MOD NO. | DRN BY. | CHKD. | APPD. | STATUS
USED ON | C UOB-HEP 20 15

H.H.WILLS PHYSICS LAB, TYNDALL AVE, BRISTOL, BS8 1TL.

UNIVERSITY OF BRISTOL
HIGH ENERGY PHYSICS GROUP
TITLE
MODULE: ltm9007_input_filter_v2

MODULE PAGE: 1 OF 1
OVERALL PAGE: 39 OF 99

Fri Apr 21 10:51:29 | 2017

D. CUSSANS

ISSUE | DATE | MOD NO. | DRN BY. | CHKD. | APPD. | STATUS
USED ON | C UOB-HEP 20 15

H.H.WILLS PHYSICS LAB, TYNDALL AVE, BRISTOL, BS8 1TL.

AFILT+ AIN- AIN+

Fri Apr 21 10:51:29 | 2017

D. CUSSANS

ISSUE | DATE | MOD NO. | DRN BY. | CHKD. | APPD. | STATUS
USED ON | C UOB-HEP 20 15

H.H.WILLS PHYSICS LAB, TYNDALL AVE, BRISTOL, BS8 1TL.

UNIVERSITY OF BRISTOL
HIGH ENERGY PHYSICS GROUP
TITLE
MODULE: ltm9007_8chan_v2

MODULE PAGE: 2 OF 2
OVERALL PAGE: 41 OF 99

FILTER; FOR ADC INPUTS; uob_hep_pc051a_lib; AIN-; AFILT+ AFILT- AIN+; C6_3 C5_3 OUT; OUT; UOB-HEP

Fri Apr 21 10:51:28 | 2017

D. CUSSANS

ISSUE | DATE | MOD NO. | DRN BY. | CHKD. | APPD. | STATUS
USED ON | C UOB-HEP 20 15

H.H.WILLS PHYSICS LAB, TYNDALL AVE, BRISTOL, BS8 1TL.

UNIVERSITY OF BRISTOL
HIGH ENERGY PHYSICS GROUP
TITLE
MODULE: ltm9007_input_filter_v2

MODULE PAGE: 1 OF 1
OVERALL PAGE: 42 OF 99

Fri Apr 21 10:51:28 | 2017

D. CUSSANS

ISSUE | DATE | MOD NO. | DRN BY. | CHKD. | APPD. | STATUS
USED ON | C UOB-HEP 20 15

H.H.WILLS PHYSICS LAB, TYNDALL AVE, BRISTOL, BS8 1TL.

UNIVERSITY OF BRISTOL
HIGH ENERGY PHYSICS GROUP
TITLE
MODULE: ltm9007_input_filter_v2

MODULE PAGE: 1 OF 1
OVERALL PAGE: 43 OF 99

Fri Apr 21 10:51:28 | 2017

D. CUSSANS

ISSUE | DATE | MOD NO. | DRN BY. | CHKD. | APPD. | STATUS
USED ON | C UOB-HEP 20 15

H.H.WILLS PHYSICS LAB, TYNDALL AVE, BRISTOL, BS8 1TL.

UNIVERSITY OF BRISTOL
HIGH ENERGY PHYSICS GROUP
TITLE
MODULE: ltm9007_input_filter_v2

MODULE PAGE: 1 OF 1
OVERALL PAGE: 44 OF 99

Fri Apr 21 10:51:28 | 2017

D. CUSSANS

ISSUE | DATE | MOD NO. | DRN BY. | CHKD. | APPD. | STATUS
USED ON | C UOB-HEP 20 15

H.H.WILLS PHYSICS LAB, TYNDALL AVE, BRISTOL, BS8 1TL.

UNIVERSITY OF BRISTOL
HIGH ENERGY PHYSICS GROUP
TITLE
MODULE: ltm9007_input_filter_v2

MODULE PAGE: 1 OF 1
OVERALL PAGE: 45 OF 99

Fri Apr 21 10:51:28 | 2017

D. CUSSANS

ISSUE | DATE | MOD NO. | DRN BY. | CHKD. | APPD. | STATUS
USED ON | C UOB-HEP 20 15

H.H.WILLS PHYSICS LAB, TYNDALL AVE, BRISTOL, BS8 1TL.

UNIVERSITY OF BRISTOL
HIGH ENERGY PHYSICS GROUP
TITLE
MODULE: ltm9007_input_filter_v2

MODULE PAGE: 1 OF 1
OVERALL PAGE: 46 OF 99

Fri Apr 21 10:51:28 | 2017

D. CUSSANS

ISSUE | DATE | MOD NO. | DRN BY. | CHKD. | APPD. | STATUS
USED ON | C UOB-HEP 20 15

H.H.WILLS PHYSICS LAB, TYNDALL AVE, BRISTOL, BS8 1TL.

UNIVERSITY OF BRISTOL
HIGH ENERGY PHYSICS GROUP
TITLE
MODULE: ltm9007_input_filter_v2

MODULE PAGE: 1 OF 1
OVERALL PAGE: 47 OF 99

Fri Apr 21 10:51:28 | 2017

D. CUSSANS

ISSUE | DATE | MOD NO. | DRN BY. | CHKD. | APPD. | STATUS
USED ON | C UOB-HEP 20 15

H.H.WILLS PHYSICS LAB, TYNDALL AVE, BRISTOL, BS8 1TL.

UNIVERSITY OF BRISTOL
HIGH ENERGY PHYSICS GROUP
TITLE
MODULE: ltm9007_input_filter_v2

MODULE PAGE: 1 OF 1
OVERALL PAGE: 48 OF 99

Fri Apr 21 10:51:28 | 2017

D. CUSSANS

ISSUE | DATE | MOD NO. | DRN BY. | CHKD. | APPD. | STATUS
USED ON | C UOB-HEP 20 15

H.H.WILLS PHYSICS LAB, TYNDALL AVE, BRISTOL, BS8 1TL.

UNIVERSITY OF BRISTOL
HIGH ENERGY PHYSICS GROUP
TITLE
MODULE: ltm9007_input_filter_v2

MODULE PAGE: 1 OF 1
OVERALL PAGE: 49 OF 99

Fri Apr 21 10:51:29 | 2017

D. CUSSANS

ISSUE | DATE | MOD NO. | DRN BY. | CHKD. | APPD. | STATUS
USED ON | C UOB-HEP 20 15

H.H.WILLS PHYSICS LAB, TYNDALL AVE, BRISTOL, BS8 1TL.

AFILT+ AIN- AIN+

Fri Apr 21 10:51:29 | 2017

D. CUSSANS

ISSUE | DATE | MOD NO. | DRN BY. | CHKD. | APPD. | STATUS
USED ON | C UOB-HEP 20 15

H.H.WILLS PHYSICS LAB, TYNDALL AVE, BRISTOL, BS8 1TL.

UNIVERSITY OF BRISTOL
HIGH ENERGY PHYSICS GROUP
TITLE
MODULE: ltm9007_8chan_v2

MODULE PAGE: 2 OF 2
OVERALL PAGE: 51 OF 99

Fri Apr 21 10:51:28 | 2017

D. CUSSANS

ISSUE | DATE | MOD NO. | DRN BY. | CHKD. | APPD. | STATUS
USED ON | C UOB-HEP 20 15

H.H.WILLS PHYSICS LAB, TYNDALL AVE, BRISTOL, BS8 1TL.

UNIVERSITY OF BRISTOL
HIGH ENERGY PHYSICS GROUP
TITLE
MODULE: ltm9007_input_filter_v2

MODULE PAGE: 1 OF 1
OVERALL PAGE: 52 OF 99

FILTER; FOR ADC INPUTS; uob_hep_pc051a_lib; AIN-; AFILT+ AFILT- AIN+; C20_4 C13_4 OUT; OUT; UOB-HEP

Fri Apr 21 10:51:28 | 2017

D. CUSSANS

ISSUE | DATE | MOD NO. | DRN BY. | CHKD. | APPD. | STATUS
USED ON | C UOB-HEP 20 15

H.H.WILLS PHYSICS LAB, TYNDALL AVE, BRISTOL, BS8 1TL.

UNIVERSITY OF BRISTOL
HIGH ENERGY PHYSICS GROUP
TITLE
MODULE: ltm9007_input_filter_v2

MODULE PAGE: 1 OF 1
OVERALL PAGE: 53 OF 99

Fri Apr 21 10:51:28 | 2017

D. CUSSANS

ISSUE | DATE | MOD NO. | DRN BY. | CHKD. | APPD. | STATUS
USED ON | C UOB-HEP 20 15

H.H.WILLS PHYSICS LAB, TYNDALL AVE, BRISTOL, BS8 1TL.

UNIVERSITY OF BRISTOL
HIGH ENERGY PHYSICS GROUP
TITLE
MODULE: ltm9007_input_filter_v2

MODULE PAGE: 1 OF 1
OVERALL PAGE: 54 OF 99

Fri Apr 21 10:51:28 | 2017

D. CUSSANS

ISSUE | DATE | MOD NO. | DRN BY. | CHKD. | APPD. | STATUS
USED ON | C UOB-HEP 20 15

H.H.WILLS PHYSICS LAB, TYNDALL AVE, BRISTOL, BS8 1TL.

UNIVERSITY OF BRISTOL
HIGH ENERGY PHYSICS GROUP
TITLE
MODULE: ltm9007_input_filter_v2

MODULE PAGE: 1 OF 1
OVERALL PAGE: 55 OF 99

Fri Apr 21 10:51:28 | 2017

D. CUSSANS

ISSUE | DATE | MOD NO. | DRN BY. | CHKD. | APPD. | STATUS
USED ON | C UOB-HEP 20 15

H.H.WILLS PHYSICS LAB, TYNDALL AVE, BRISTOL, BS8 1TL.

UNIVERSITY OF BRISTOL
HIGH ENERGY PHYSICS GROUP
TITLE
MODULE: ltm9007_input_filter_v2

MODULE PAGE: 1 OF 1
OVERALL PAGE: 56 OF 99

Fri Apr 21 10:51:28 | 2017

D. CUSSANS

ISSUE | DATE | MOD NO. | DRN BY. | CHKD. | APPD. | STATUS
USED ON | C UOB-HEP 20 15

H.H.WILLS PHYSICS LAB, TYNDALL AVE, BRISTOL, BS8 1TL.

UNIVERSITY OF BRISTOL
HIGH ENERGY PHYSICS GROUP
TITLE
MODULE: ltm9007_input_filter_v2

MODULE PAGE: 1 OF 1
OVERALL PAGE: 57 OF 99

Fri Apr 21 10:51:28 | 2017

D. CUSSANS

ISSUE | DATE | MOD NO. | DRN BY. | CHKD. | APPD. | STATUS
USED ON | C UOB-HEP 20 15

H.H.WILLS PHYSICS LAB, TYNDALL AVE, BRISTOL, BS8 1TL.

UNIVERSITY OF BRISTOL
HIGH ENERGY PHYSICS GROUP
TITLE
MODULE: ltm9007_input_filter_v2

MODULE PAGE: 1 OF 1
OVERALL PAGE: 58 OF 99

Fri Apr 21 10:51:28 | 2017

D. CUSSANS

ISSUE | DATE | MOD NO. | DRN BY. | CHKD. | APPD. | STATUS
USED ON | C UOB-HEP 20 15

H.H.WILLS PHYSICS LAB, TYNDALL AVE, BRISTOL, BS8 1TL.

UNIVERSITY OF BRISTOL
HIGH ENERGY PHYSICS GROUP
TITLE
MODULE: ltm9007_input_filter_v2

MODULE PAGE: 1 OF 1
OVERALL PAGE: 59 OF 99

Fri Apr 21 10:51:29 | 2017

D. CUSSANS

ISSUE | DATE | MOD NO. | DRN BY. | CHKD. | APPD. | STATUS
USED ON | C UOB-HEP 20 15

H.H.WILLS PHYSICS LAB, TYNDALL AVE, BRISTOL, BS8 1TL.

AFILT+ AIN- AIN+

Fri Apr 21 10:51:29 | 2017

D. CUSSANS

ISSUE | DATE | MOD NO. | DRN BY. | CHKD. | APPD. | STATUS
USED ON | C UOB-HEP 20 15

H.H.WILLS PHYSICS LAB, TYNDALL AVE, BRISTOL, BS8 1TL.

UNIVERSITY OF BRISTOL
HIGH ENERGY PHYSICS GROUP
TITLE
MODULE: ltm9007_8chan_v2

MODULE PAGE: 2 OF 2
OVERALL PAGE: 61 OF 99

Fri Apr 21 10:51:28 | 2017

D. CUSSANS

ISSUE | DATE | MOD NO. | DRN BY. | CHKD. | APPD. | STATUS
USED ON | C UOB-HEP 20 15

H.H.WILLS PHYSICS LAB, TYNDALL AVE, BRISTOL, BS8 1TL.

UNIVERSITY OF BRISTOL
HIGH ENERGY PHYSICS GROUP
TITLE
MODULE: ltm9007_input_filter_v2

MODULE PAGE: 1 OF 1
OVERALL PAGE: 62 OF 99

FILTER; FOR ADC INPUTS; uob_hep_pc051a_lib; AIN-; AFILT+ AFILT- AIN+; C20_6 C13_6 OUT; OUT; UOB-HEP

Fri Apr 21 10:51:28 | 2017

D. CUSSANS

ISSUE | DATE | MOD NO. | DRN BY. | CHKD. | APPD. | STATUS
USED ON | C UOB-HEP 20 15

H.H.WILLS PHYSICS LAB, TYNDALL AVE, BRISTOL, BS8 1TL.

UNIVERSITY OF BRISTOL
HIGH ENERGY PHYSICS GROUP
TITLE
MODULE: ltm9007_input_filter_v2

MODULE PAGE: 1 OF 1
OVERALL PAGE: 63 OF 99

Fri Apr 21 10:51:28 | 2017

D. CUSSANS

ISSUE | DATE | MOD NO. | DRN BY. | CHKD. | APPD. | STATUS
USED ON | C UOB-HEP 20 15

H.H.WILLS PHYSICS LAB, TYNDALL AVE, BRISTOL, BS8 1TL.

UNIVERSITY OF BRISTOL
HIGH ENERGY PHYSICS GROUP
TITLE
MODULE: ltm9007_input_filter_v2

MODULE PAGE: 1 OF 1
OVERALL PAGE: 64 OF 99

Fri Apr 21 10:51:28 | 2017

D. CUSSANS

ISSUE | DATE | MOD NO. | DRN BY. | CHKD. | APPD. | STATUS
USED ON | C UOB-HEP 20 15

H.H.WILLS PHYSICS LAB, TYNDALL AVE, BRISTOL, BS8 1TL.

UNIVERSITY OF BRISTOL
HIGH ENERGY PHYSICS GROUP
TITLE
MODULE: ltm9007_input_filter_v2

MODULE PAGE: 1 OF 1
OVERALL PAGE: 65 OF 99

Fri Apr 21 10:51:28 | 2017

D. CUSSANS

ISSUE | DATE | MOD NO. | DRN BY. | CHKD. | APPD. | STATUS
USED ON | C UOB-HEP 20 15

H.H.WILLS PHYSICS LAB, TYNDALL AVE, BRISTOL, BS8 1TL.

UNIVERSITY OF BRISTOL
HIGH ENERGY PHYSICS GROUP
TITLE
MODULE: ltm9007_input_filter_v2

MODULE PAGE: 1 OF 1
OVERALL PAGE: 66 OF 99

Fri Apr 21 10:51:28 | 2017

D. CUSSANS

ISSUE | DATE | MOD NO. | DRN BY. | CHKD. | APPD. | STATUS
USED ON | C UOB-HEP 20 15

H.H.WILLS PHYSICS LAB, TYNDALL AVE, BRISTOL, BS8 1TL.

UNIVERSITY OF BRISTOL
HIGH ENERGY PHYSICS GROUP
TITLE
MODULE: ltm9007_input_filter_v2

MODULE PAGE: 1 OF 1
OVERALL PAGE: 67 OF 99

Fri Apr 21 10:51:28 | 2017

D. CUSSANS

ISSUE | DATE | MOD NO. | DRN BY. | CHKD. | APPD. | STATUS
USED ON | C UOB-HEP 20 15

H.H.WILLS PHYSICS LAB, TYNDALL AVE, BRISTOL, BS8 1TL.

UNIVERSITY OF BRISTOL
HIGH ENERGY PHYSICS GROUP
TITLE
MODULE: ltm9007_input_filter_v2

MODULE PAGE: 1 OF 1
OVERALL PAGE: 68 OF 99

Fri Apr 21 10:51:28 | 2017

D. CUSSANS

ISSUE | DATE | MOD NO. | DRN BY. | CHKD. | APPD. | STATUS
USED ON | C UOB-HEP 20 15

H.H.WILLS PHYSICS LAB, TYNDALL AVE, BRISTOL, BS8 1TL.

UNIVERSITY OF BRISTOL
HIGH ENERGY PHYSICS GROUP
TITLE
MODULE: ltm9007_input_filter_v2

MODULE PAGE: 1 OF 1
OVERALL PAGE: 69 OF 99

Fri Apr 21 10:51:29 | 2017

D. CUSSANS

ISSUE | DATE | MOD NO. | DRN BY. | CHKD. | APPD. | STATUS
USED ON | C UOB-HEP 20 15

H.H.WILLS PHYSICS LAB, TYNDALL AVE, BRISTOL, BS8 1TL.

AFILT+ AIN- AIN+

Fri Apr 21 10:51:29 | 2017

D. CUSSANS

ISSUE | DATE | MOD NO. | DRN BY. | CHKD. | APPD. | STATUS
USED ON | C UOB-HEP 20 15

H.H.WILLS PHYSICS LAB, TYNDALL AVE, BRISTOL, BS8 1TL.

UNIVERSITY OF BRISTOL
HIGH ENERGY PHYSICS GROUP
TITLE
MODULE: ltm9007_8chan_v2

MODULE PAGE: 2 OF 2
OVERALL PAGE: 71 OF 99

Fri Apr 21 10:51:28 | 2017

D. CUSSANS

ISSUE | DATE | MOD NO. | DRN BY. | CHKD. | APPD. | STATUS
USED ON | C UOB-HEP 20 15

H.H.WILLS PHYSICS LAB, TYNDALL AVE, BRISTOL, BS8 1TL.

UNIVERSITY OF BRISTOL
HIGH ENERGY PHYSICS GROUP
TITLE
MODULE: ltm9007_input_filter_v2

MODULE PAGE: 1 OF 1
OVERALL PAGE: 72 OF 99

Fri Apr 21 10:51:28 | 2017

D. CUSSANS

ISSUE | DATE | MOD NO. | DRN BY. | CHKD. | APPD. | STATUS
USED ON | C UOB-HEP 20 15

H.H.WILLS PHYSICS LAB, TYNDALL AVE, BRISTOL, BS8 1TL.

UNIVERSITY OF BRISTOL
HIGH ENERGY PHYSICS GROUP
TITLE
MODULE: ltm9007_input_filter_v2

MODULE PAGE: 1 OF 1
OVERALL PAGE: 73 OF 99

FILTER; FOR ADC INPUTS; uob_hep_pc051a_lib; AIN-; AFILT+ AFILT- AIN+; C21_7 C14_7 OUT; OUT; UOB-HEP

Fri Apr 21 10:51:28 | 2017

D. CUSSANS

ISSUE | DATE | MOD NO. | DRN BY. | CHKD. | APPD. | STATUS
USED ON | C UOB-HEP 20 15

H.H.WILLS PHYSICS LAB, TYNDALL AVE, BRISTOL, BS8 1TL.

UNIVERSITY OF BRISTOL
HIGH ENERGY PHYSICS GROUP
TITLE
MODULE: ltm9007_input_filter_v2

MODULE PAGE: 1 OF 1
OVERALL PAGE: 74 OF 99

Fri Apr 21 10:51:28 | 2017

D. CUSSANS

ISSUE | DATE | MOD NO. | DRN BY. | CHKD. | APPD. | STATUS
USED ON | C UOB-HEP 20 15

H.H.WILLS PHYSICS LAB, TYNDALL AVE, BRISTOL, BS8 1TL.

UNIVERSITY OF BRISTOL
HIGH ENERGY PHYSICS GROUP
TITLE
MODULE: ltm9007_input_filter_v2

MODULE PAGE: 1 OF 1
OVERALL PAGE: 75 OF 99

Fri Apr 21 10:51:28 | 2017

D. CUSSANS

ISSUE | DATE | MOD NO. | DRN BY. | CHKD. | APPD. | STATUS
USED ON | C UOB-HEP 20 15

H.H.WILLS PHYSICS LAB, TYNDALL AVE, BRISTOL, BS8 1TL.

UNIVERSITY OF BRISTOL
HIGH ENERGY PHYSICS GROUP
TITLE
MODULE: ltm9007_input_filter_v2

MODULE PAGE: 1 OF 1
OVERALL PAGE: 76 OF 99

Fri Apr 21 10:51:28 | 2017

D. CUSSANS

ISSUE | DATE | MOD NO. | DRN BY. | CHKD. | APPD. | STATUS
USED ON | C UOB-HEP 20 15

H.H.WILLS PHYSICS LAB, TYNDALL AVE, BRISTOL, BS8 1TL.

UNIVERSITY OF BRISTOL
HIGH ENERGY PHYSICS GROUP
TITLE
MODULE: ltm9007_input_filter_v2

MODULE PAGE: 1 OF 1
OVERALL PAGE: 77 OF 99

Fri Apr 21 10:51:28 | 2017

D. CUSSANS

ISSUE | DATE | MOD NO. | DRN BY. | CHKD. | APPD. | STATUS
USED ON | C UOB-HEP 20 15

H.H.WILLS PHYSICS LAB, TYNDALL AVE, BRISTOL, BS8 1TL.

UNIVERSITY OF BRISTOL
HIGH ENERGY PHYSICS GROUP
TITLE
MODULE: ltm9007_input_filter_v2

MODULE PAGE: 1 OF 1
OVERALL PAGE: 78 OF 99

Fri Apr 21 10:51:28 | 2017

D. CUSSANS

ISSUE | DATE | MOD NO. | DRN BY. | CHKD. | APPD. | STATUS
USED ON | C UOB-HEP 20 15

H.H.WILLS PHYSICS LAB, TYNDALL AVE, BRISTOL, BS8 1TL.

UNIVERSITY OF BRISTOL
HIGH ENERGY PHYSICS GROUP
TITLE
MODULE: ltm9007_input_filter_v2

MODULE PAGE: 1 OF 1
OVERALL PAGE: 79 OF 99

Fri Apr 21 10:51:29 | 2017

D. CUSSANS

ISSUE | DATE | MOD NO. | DRN BY. | CHKD. | APPD. | STATUS
USED ON | C UOB-HEP 20 15

H.H.WILLS PHYSICS LAB, TYNDALL AVE, BRISTOL, BS8 1TL.

AFILT+ AIN- AIN+

Fri Apr 21 10:51:29 | 2017

D. CUSSANS

ISSUE | DATE | MOD NO. | DRN BY. | CHKD. | APPD. | STATUS
USED ON | C UOB-HEP 20 15

H.H.WILLS PHYSICS LAB, TYNDALL AVE, BRISTOL, BS8 1TL.

UNIVERSITY OF BRISTOL
HIGH ENERGY PHYSICS GROUP
TITLE
MODULE: ltm9007_8chan_v2

MODULE PAGE: 2 OF 2
OVERALL PAGE: 81 OF 99

Fri Apr 21 10:51:28 | 2017

D. CUSSANS

ISSUE | DATE | MOD NO. | DRN BY. | CHKD. | APPD. | STATUS
USED ON | C UOB-HEP 20 15

H.H.WILLS PHYSICS LAB, TYNDALL AVE, BRISTOL, BS8 1TL.

UNIVERSITY OF BRISTOL
HIGH ENERGY PHYSICS GROUP
TITLE
MODULE: ltm9007_input_filter_v2

MODULE PAGE: 1 OF 1
OVERALL PAGE: 82 OF 99

Fri Apr 21 10:51:28 | 2017

D. CUSSANS

ISSUE | DATE | MOD NO. | DRN BY. | CHKD. | APPD. | STATUS
USED ON | C UOB-HEP 20 15

H.H.WILLS PHYSICS LAB, TYNDALL AVE, BRISTOL, BS8 1TL.

UNIVERSITY OF BRISTOL
HIGH ENERGY PHYSICS GROUP
TITLE
MODULE: ltm9007_input_filter_v2

MODULE PAGE: 1 OF 1
OVERALL PAGE: 83 OF 99

FILTER; FOR ADC INPUTS; uob_hep_pc051a_lib; AIN-; AFILT+ AFILT- AIN+; C21_8 C14_8 OUT; OUT; UOB-HEP

Fri Apr 21 10:51:28 | 2017

D. CUSSANS

ISSUE | DATE | MOD NO. | DRN BY. | CHKD. | APPD. | STATUS
USED ON | C UOB-HEP 20 15

H.H.WILLS PHYSICS LAB, TYNDALL AVE, BRISTOL, BS8 1TL.

UNIVERSITY OF BRISTOL
HIGH ENERGY PHYSICS GROUP
TITLE
MODULE: ltm9007_input_filter_v2

MODULE PAGE: 1 OF 1
OVERALL PAGE: 84 OF 99

Fri Apr 21 10:51:28 | 2017

D. CUSSANS

ISSUE | DATE | MOD NO. | DRN BY. | CHKD. | APPD. | STATUS
USED ON | C UOB-HEP 20 15

H.H.WILLS PHYSICS LAB, TYNDALL AVE, BRISTOL, BS8 1TL.

UNIVERSITY OF BRISTOL
HIGH ENERGY PHYSICS GROUP
TITLE
MODULE: ltm9007_input_filter_v2

MODULE PAGE: 1 OF 1
OVERALL PAGE: 85 OF 99

Fri Apr 21 10:51:28 | 2017

D. CUSSANS

ISSUE | DATE | MOD NO. | DRN BY. | CHKD. | APPD. | STATUS
USED ON | C UOB-HEP 20 15

H.H.WILLS PHYSICS LAB, TYNDALL AVE, BRISTOL, BS8 1TL.

UNIVERSITY OF BRISTOL
HIGH ENERGY PHYSICS GROUP
TITLE
MODULE: ltm9007_input_filter_v2

MODULE PAGE: 1 OF 1
OVERALL PAGE: 86 OF 99

Fri Apr 21 10:51:28 | 2017

D. CUSSANS

ISSUE | DATE | MOD NO. | DRN BY. | CHKD. | APPD. | STATUS
USED ON | C UOB-HEP 20 15

H.H.WILLS PHYSICS LAB, TYNDALL AVE, BRISTOL, BS8 1TL.

UNIVERSITY OF BRISTOL
HIGH ENERGY PHYSICS GROUP
TITLE
MODULE: ltm9007_input_filter_v2

MODULE PAGE: 1 OF 1
OVERALL PAGE: 87 OF 99

Fri Apr 21 10:51:28 | 2017

D. CUSSANS

ISSUE | DATE | MOD NO. | DRN BY. | CHKD. | APPD. | STATUS
USED ON | C UOB-HEP 20 15

H.H.WILLS PHYSICS LAB, TYNDALL AVE, BRISTOL, BS8 1TL.

UNIVERSITY OF BRISTOL
HIGH ENERGY PHYSICS GROUP
TITLE
MODULE: ltm9007_input_filter_v2

MODULE PAGE: 1 OF 1
OVERALL PAGE: 88 OF 99

Fri Apr 21 10:51:28 | 2017

D. CUSSANS

ISSUE | DATE | MOD NO. | DRN BY. | CHKD. | APPD. | STATUS
USED ON | C UOB-HEP 20 15

H.H.WILLS PHYSICS LAB, TYNDALL AVE, BRISTOL, BS8 1TL.

UNIVERSITY OF BRISTOL
HIGH ENERGY PHYSICS GROUP
TITLE
MODULE: ltm9007_input_filter_v2

MODULE PAGE: 1 OF 1
OVERALL PAGE: 89 OF 99

Fri Apr 21 10:51:29 | 2017

D. CUSSANS

ISSUE | DATE | MOD NO. | DRN BY. | CHKD. | APPD. | STATUS
USED ON | C UOB-HEP 20 15

H.H.WILLS PHYSICS LAB, TYNDALL AVE, BRISTOL, BS8 1TL.

AFILT+ AIN- AIN+

Fri Apr 21 10:51:29 | 2017

D. CUSSANS

ISSUE | DATE | MOD NO. | DRN BY. | CHKD. | APPD. | STATUS
USED ON | C UOB-HEP 20 15

H.H.WILLS PHYSICS LAB, TYNDALL AVE, BRISTOL, BS8 1TL.

UNIVERSITY OF BRISTOL
HIGH ENERGY PHYSICS GROUP
TITLE
MODULE: ltm9007_8chan_v2

MODULE PAGE: 2 OF 2
OVERALL PAGE: 91 OF 99

Fri Apr 21 10:51:28 | 2017

D. CUSSANS

ISSUE | DATE | MOD NO. | DRN BY. | CHKD. | APPD. | STATUS
USED ON | C UOB-HEP 20 15

H.H.WILLS PHYSICS LAB, TYNDALL AVE, BRISTOL, BS8 1TL.

UNIVERSITY OF BRISTOL
HIGH ENERGY PHYSICS GROUP
TITLE
MODULE: ltm9007_input_filter_v2

MODULE PAGE: 1 OF 1
OVERALL PAGE: 92 OF 99

Fri Apr 21 10:51:28 | 2017

D. CUSSANS

ISSUE | DATE | MOD NO. | DRN BY. | CHKD. | APPD. | STATUS
USED ON | C UOB-HEP 20 15

H.H.WILLS PHYSICS LAB, TYNDALL AVE, BRISTOL, BS8 1TL.

UNIVERSITY OF BRISTOL
HIGH ENERGY PHYSICS GROUP
TITLE
MODULE: ltm9007_input_filter_v2

MODULE PAGE: 1 OF 1
OVERALL PAGE: 93 OF 99

FILTER; FOR ADC INPUTS; uob_hep_pc051a_lib; AIN-; AFILT+ AFILT- AIN+; C21_9 C14_9 OUT; OUT; UOB-HEP

Fri Apr 21 10:51:28 | 2017

D. CUSSANS

ISSUE | DATE | MOD NO. | DRN BY. | CHKD. | APPD. | STATUS
USED ON | C UOB-HEP 20 15

H.H.WILLS PHYSICS LAB, TYNDALL AVE, BRISTOL, BS8 1TL.

UNIVERSITY OF BRISTOL
HIGH ENERGY PHYSICS GROUP
TITLE
MODULE: ltm9007_input_filter_v2

MODULE PAGE: 1 OF 1
OVERALL PAGE: 94 OF 99

Fri Apr 21 10:51:28 | 2017

D. CUSSANS

ISSUE | DATE | MOD NO. | DRN BY. | CHKD. | APPD. | STATUS
USED ON | C UOB-HEP 20 15

H.H.WILLS PHYSICS LAB, TYNDALL AVE, BRISTOL, BS8 1TL.

UNIVERSITY OF BRISTOL
HIGH ENERGY PHYSICS GROUP
TITLE
MODULE: ltm9007_input_filter_v2

MODULE PAGE: 1 OF 1
OVERALL PAGE: 95 OF 99

Fri Apr 21 10:51:28 | 2017

D. CUSSANS

ISSUE | DATE | MOD NO. | DRN BY. | CHKD. | APPD. | STATUS
USED ON | C UOB-HEP 20 15

H.H.WILLS PHYSICS LAB, TYNDALL AVE, BRISTOL, BS8 1TL.

UNIVERSITY OF BRISTOL
HIGH ENERGY PHYSICS GROUP
TITLE
MODULE: ltm9007_input_filter_v2

MODULE PAGE: 1 OF 1
OVERALL PAGE: 96 OF 99

Fri Apr 21 10:51:28 | 2017

D. CUSSANS

ISSUE | DATE | MOD NO. | DRN BY. | CHKD. | APPD. | STATUS
USED ON | C UOB-HEP 20 15

H.H.WILLS PHYSICS LAB, TYNDALL AVE, BRISTOL, BS8 1TL.

UNIVERSITY OF BRISTOL
HIGH ENERGY PHYSICS GROUP
TITLE
MODULE: ltm9007_input_filter_v2

MODULE PAGE: 1 OF 1
OVERALL PAGE: 97 OF 99

Fri Apr 21 10:51:28 | 2017

D. CUSSANS

ISSUE | DATE | MOD NO. | DRN BY. | CHKD. | APPD. | STATUS
USED ON | C UOB-HEP 20 15

H.H.WILLS PHYSICS LAB, TYNDALL AVE, BRISTOL, BS8 1TL.

UNIVERSITY OF BRISTOL
HIGH ENERGY PHYSICS GROUP
TITLE
MODULE: ltm9007_input_filter_v2

MODULE PAGE: 1 OF 1
OVERALL PAGE: 98 OF 99

Fri Apr 21 10:51:28 | 2017

D. CUSSANS

ISSUE | DATE | MOD NO. | DRN BY. | CHKD. | APPD. | STATUS
USED ON | C UOB-HEP 20 15

H.H.WILLS PHYSICS LAB, TYNDALL AVE, BRISTOL, BS8 1TL.

UNIVERSITY OF BRISTOL
HIGH ENERGY PHYSICS GROUP
TITLE
MODULE: ltm9007_input_filter_v2

MODULE PAGE: 1 OF 1
OVERALL PAGE: 99 OF 99

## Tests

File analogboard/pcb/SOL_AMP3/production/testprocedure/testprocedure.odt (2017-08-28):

# version history

version 0.2

Last saved date : 2 Aug 2017 17:25:46

version 0.1 initial proposal 20 Jan 2017 14:08:16

# introduction

One of the boards of the first production batch should be checked careful by an expert to see that it is 100 % correct. So this action should spot eventual wrong resistor values and eventual wrong capacitors in the signal path. It is harder to spot wrong decoupling capacitor values.
This board will be used to generate the acceptance values for the measurements below. Or min / max values for simple measurement or templates for pulse responses.
For new batches the DC output values and the VCOM should be measured for one board to spot wrong resistor values as this is not so easy to spot in the procedure below .

The test procedure below should identify none conformities of the production. So mainly bad soldering , shorts , open connections .

## general remarks

The DUT is powered via the test board. ( TBRD)

Power for the TBRD : + 5.3 V ~ .5 A , - 3.3 V ~ .5 A

All measurements should be stored . This will not be done for the first 20 board because of time limitations. We have to decide afterwards if we need this information.

# Procedure

## Start-up :

The startup procedure should give an first indication that all active components are correctly working.

- Connect the DUT to the test board , make sure the jumper of the power enable line is not connected. ( red in fig
- Program addresses trim DAC's
  - connect the LDA lines to the corresponding test holes
  - set 10 values for each DAC output and measure ( via processor ) This test should confirm the correct working of the trim DAC's
- Remove I2C
- power off

## Signal response measurement

connect amplifier board( connected to the TBRD) to ADC board (64 chan)

- activate the power to the DUT
- set the power cntrl line of the DUT via the ADC board
- check I2C functionality This test should conform the full functionality of the I2C lines and communication with the devices.
  - check one value for the bias
  - check one value for the trim DAC's
  - check the temperature and read the ee-prom
- check the pedestal and rms accept 90 -- 110% This should spot wrong connection in the offset circuit and / or Vcom etc. Not clear if all these are covered with this test.
- check signal response These test should confirm ( much as can be detected) that all coupling capacitors are correctly soldered and that the signal resistors and capacitors are correct.
  - sine differential 100K 500 K , 1 M , 2 M, 4 . 8 14 MHz xmV for group 1 then for group 2
    - check signal for group 1 ( in respect to template)
    - check signal for group 2 ( cross talk)
  - Step function (input is saw waveform , need triggered software )
    - different amplitudes
      - check pulse response ( need template for different amplitudes
  - common mode 100K 500 K , 1 M , 2 M 4 , 8 14 MHz for group 1 then for group 2 This should spot mismatches for the components in the signal path
  - Power supply rejection 100K 500 K , 1 M , 2 M, 4 . 8 14 MHz This eventual can spot bad decoupling capacitors .

power off

Not covered by these tests :

- de-coupling capacitors of the I2C devices. Not clear if this can be tested at all.

## fix ID

In case test passed :

- remove from ADC board
- power the board
- connect I2C , set ee-prom values ( serial nr etc)
- power off the board for 10 s
- power the board
- read back ee-prom check if ok
- power off the board
- connect the lock lines
- power the board
- lock the ee-prom
- power off the board
- power the board
- read back the ee-prom
- write 0 to ee-prom
- read back ee-prom ( check not 0)

done ..

version 0.2 wim.beaumont@uantwerpen.be 4/4

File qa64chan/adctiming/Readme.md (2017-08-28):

In order to run this program you first need to compile saffron. 

Elsewhere do:

````
git clone git@bitbucket.org/solidexperiment/saffron2
cd saffron2
git checkout qa64ch
source getmysql.sh
make
````

The copy the saffron executable to this directory.

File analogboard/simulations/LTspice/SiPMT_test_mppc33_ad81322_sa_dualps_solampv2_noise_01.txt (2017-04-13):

frequency	V(onoise)
1.000000000000000e+03	9.674508e-09
1.071773462536293e+03	9.410053e-09
1.148698354997035e+03	9.156459e-09
1.231144413344916e+03	8.913440e-09
1.319507910772894e+03	8.680708e-09
1.414213562373095e+03	8.457969e-09
1.515716566510398e+03	8.244928e-09
1.624504792712471e+03	8.041288e-09
1.741101126592248e+03	7.846752e-09
1.866065983073615e+03	7.661026e-09
2.000000000000000e+03	7.483821e-09
2.143546925072586e+03	7.314847e-09
2.297396709994070e+03	7.153823e-09
2.462288826689832e+03	7.000471e-09
2.639015821545788e+03	6.854517e-09
2.828427124746190e+03	6.715696e-09
3.031433133020796e+03	6.583748e-09
3.249009585424941e+03	6.458417e-09
3.482202253184495e+03	6.339456e-09
3.732131966147228e+03	6.226624e-09
3.999999999999999e+03	6.119686e-09
4.287093850145171e+03	6.018415e-09
4.594793419988138e+03	5.922590e-09
4.924577653379663e+03	5.831998e-09
5.278031643091575e+03	5.746432e-09
5.656854249492378e+03	5.665695e-09
6.062866266041589e+03	5.589597e-09
6.498019170849881e+03	5.517955e-09
6.964404506368989e+03	5.450595e-09
7.464263932294455e+03	5.387353e-09
7.999999999999995e+03	5.328074e-09
8.574187700290340e+03	5.272610e-09
9.189586839976275e+03	5.220828e-09
9.849155306759325e+03	5.172601e-09
1.055606328618315e+04	5.127817e-09
1.131370849898475e+04	5.086374e-09
1.212573253208318e+04	5.048184e-09
1.299603834169976e+04	5.013172e-09
1.392880901273798e+04	4.981279e-09
1.492852786458891e+04	4.952461e-09
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

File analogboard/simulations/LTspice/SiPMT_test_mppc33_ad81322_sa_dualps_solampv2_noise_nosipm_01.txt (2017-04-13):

frequency	V(onoise)
1.000000000000000e+03	9.733913e-09
1.071773462536293e+03	9.468787e-09
1.148698354997035e+03	9.214341e-09
1.231144413344916e+03	8.970318e-09
1.319507910772894e+03	8.736447e-09
1.414213562373095e+03	8.512456e-09
1.515716566510398e+03	8.298066e-09
1.624504792712471e+03	8.092996e-09
1.741101126592248e+03	7.896963e-09
1.866065983073615e+03	7.709684e-09
2.000000000000000e+03	7.530878e-09
2.143546925072586e+03	7.360263e-09
2.297396709994070e+03	7.197562e-09
2.462288826689832e+03	7.042500e-09
2.639015821545788e+03	6.894807e-09
2.828427124746190e+03	6.754218e-09
3.031433133020796e+03	6.620470e-09
3.249009585424941e+03	6.493305e-09
3.482202253184495e+03	6.372474e-09
3.732131966147228e+03	6.257728e-09
3.999999999999999e+03	6.148827e-09
4.287093850145171e+03	6.045534e-09
4.594793419988138e+03	5.947620e-09
4.924577653379663e+03	5.854860e-09
5.278031643091575e+03	5.767034e-09
5.656854249492378e+03	5.683930e-09
6.062866266041589e+03	5.605341e-09
6.498019170849881e+03	5.531064e-09
6.964404506368989e+03	5.460904e-09
7.464263932294455e+03	5.394671e-09
7.999999999999995e+03	5.332184e-09
8.574187700290340e+03	5.273262e-09
9.189586839976275e+03	5.217736e-09
9.849155306759325e+03	5.165441e-09
1.055606328618315e+04	5.116218e-09
1.131370849898475e+04	5.069914e-09
1.212573253208318e+04	5.026383e-09
1.299603834169976e+04	4.985485e-09
1.392880901273798e+04	4.947086e-09
1.492852786458891e+04	4.911060e-09
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

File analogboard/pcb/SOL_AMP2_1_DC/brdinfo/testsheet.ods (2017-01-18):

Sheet: ser2
 |  | unit |  |  |  | expected
 | serail nr |  | 2 |  |  |  |  |  |  |  |  | addr trim 4.7 |  | 3
 | version |  |  |  |  |  |  |  |  |  |  | addr trim 0-3 |  | 5
 | date
 | Vin |  | 7.1 |  | [V] | 5.3
 | Iin |  | 0.16 |  | [A] | 0.16
 | Vdd ana |  | 4.47 |  | [V] | 4.5 |  | R19 | 2.4
 | Vdd dig |  | 4.45 |  | [V] | 4.5 |  | R18 | 1
 | Vee |  | 4.45 |  | [V] | -3 |  | ratio | 0.7058823529
 | Ivee |  | 0.095 |  | [A] | 0.1
DAC |  |  |  |  |  |  |  | VDACexp | VDAC | Vset exp | Vset
 | Vbias in |  | 77.6 |  | [V] | 77.6
D00 | Vbias max @0D00 |  | 76.46 |  | [V] | 76.1 |  | 3.65625 | 3.61 | 2.5808823529 | 2.54
C9A | Vbias@ C9A |  | 74.3 |  | [V] | 75.0534237132 |  | 3.5441894531 | 3.5 | 2.5017807904 | 2.477
B8A | Vbias@ B8A |  | 67.99 |  | [V] | 68.7252987132 |  | 3.2453613281 | 3.21 | 2.2908432904 | 2.266
AAA | Vbias@ AAA |  | 62.875 |  | [V] | 63.5139016544 |  | 2.9992675781 | 2.968 | 2.1171300551 | 2.096
9AA | Vbias |  | 56.93 |  | [V] | 57.5580193015 |  | 2.7180175781 | 2.688 | 1.9186006434 | 1.898
 | Vbias @0 V |  | 36.14 |  | [V] | 37.6 |  | 0 | 0.003 | 0 | 0.003
 | ch |  | 0 |  |  | 1 |  |  | 2 |  |  | 3 |  |  | 4 |  |  | 5 |  |  | 6 |  |  | 7
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

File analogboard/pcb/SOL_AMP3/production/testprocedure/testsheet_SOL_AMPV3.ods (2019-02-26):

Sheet: Sheet1
SOLID SOL_AMPV3 ver 3.2 test sheet
test sheet version |  |  | 1 |  | 1. Aug. 2017
test sheet version |  |  | 1.1 |  | 11. Dec. 2017 |  | corrected VBS
serial nr : |  |  |  |  | TesterID
Date :
 |  |  |  |  | VHIN | voltages with 2 decimal digits |  |  |  |  |  | I2C tst
 | Voltage Switch tested
 |  |  |  |  |  |  |  |  |  |  |  | zener diodes
 | T4 | 5V nom | T5V |  | T5D |  |  | TM5 |  | TV3N
 | V5 in |  | V5 meas | V5D nom | V5D meas |  |  | V3 in | V3 nom | V3 meas
[V] |  | 4.6 |  | 4.6 |  |  |  |  | -3
[A] |  | 0.51 |  |  |  |  |  |  | 0.49 |  |  | bushes removed
 | V 1,8 | V 1.8 | Vcom | Vcom 1 | Vcom 2
 | nom | meas | nom | meas | meas |  |  |  |  |  |  | ee prom info
[V] | 1.8 |  | 0.9
HV take care
bias cntr |  |  |  | check only |  |  |  |  | check only |  |  |  |  | write down
 | DACB [V] |  |  |  |  | VBS [V] |  |  |  |  |  | VB [V]
set | Vmin | Vnom | Vmax | Vmeas |  | Vmin | Vnom | Vmax | Vmeas |  | Vmin | Vnom | Vmax | Vmax
0 | 0.00 | 0 | 0.015 |  |  | 0 | 0.00 | 0.015 |  |  | 32 | 35 | 38
50 | 2.33 | 2.38 | 2.43 |  |  | 1.65 | 1.68 | 1.71 |  |  | 49.49 | 50.5 | 51.51
65 | 3.04 | 3.1 | 3.16 |  |  | 2.14 | 2.19 | 2.23 |  |  | 64.19 | 65.5 | 66.81
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

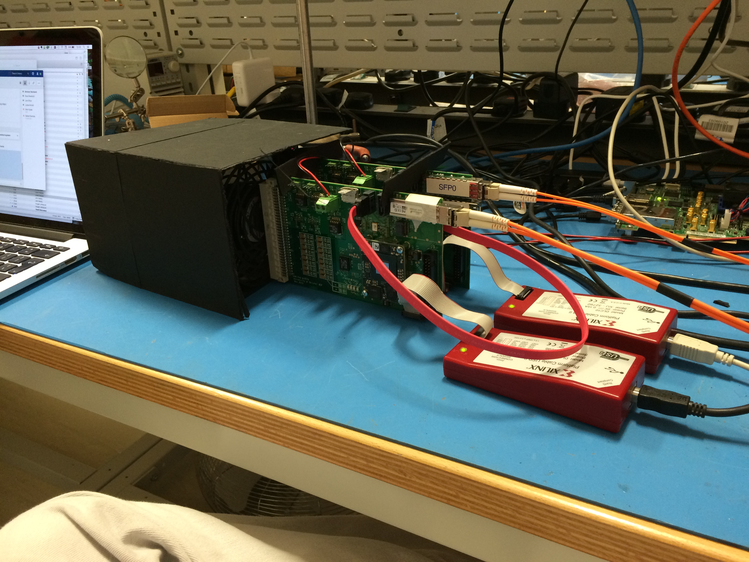
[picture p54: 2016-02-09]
digitalboard/imgs/BristolTestBench.JPG

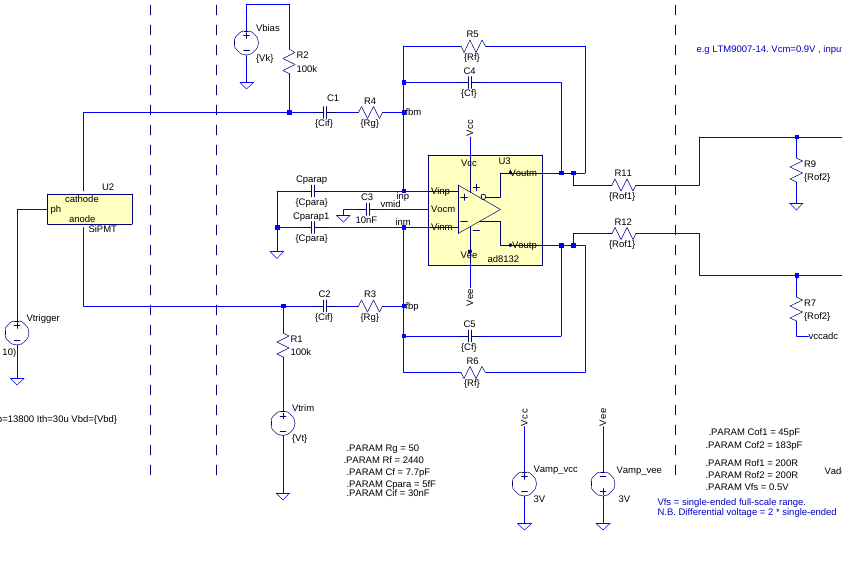
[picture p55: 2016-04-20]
docs/electronicsspec/imgs/SiPM_test_dc_schematic.png

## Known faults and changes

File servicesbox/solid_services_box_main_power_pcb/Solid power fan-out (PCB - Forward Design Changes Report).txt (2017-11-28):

Forward Design Changes Report
-----------------------------

Report File:        H:\Projects\SoLid\DCDC Test circuit\Solid Power Fanout\Solid power fan-out (PCB - Forward Design Changes Report).txt
Report Written:     Monday, October 31, 2016
Project Path:       H:\Projects\SoLid\DCDC Test circuit\Solid Power Fanout\Solid power fanout.prj
Design Path:        H:\Projects\SoLid\DCDC Test circuit\Solid Power Fanout\Solid power fan-out.pcb
Design Title:       
Created:            20/09/2016 07:58:07
Last Saved:         31/10/2016 10:10:55
Editing Time:       18631 min
Units:              mm (precision 1)

Connected pin "U48-6" to net "Bias-".
Connected pin "U48-7" to net "Bias+".
Connected pin "U48-8" to net "N0014".
Connected pin "U8-8" to net "N0106".
Connected pin "U15-8" to net "N0111".
Connected pin "U19-8" to net "N0116".
Connected pin "U23-8" to net "N0121".
Connected pin "U27-8" to net "N0130".
Connected pin "U31-8" to net "N0134".
Connected pin "U35-8" to net "N0138".
Connected pin "U39-8" to net "N0142".
Connected pin "U43-8" to net "N0146".

End Of Report.

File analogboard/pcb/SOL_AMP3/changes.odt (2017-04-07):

Changes

data 27 July 2016

corrected voltage set resistor values for the LDO's .

Changed the symbol and case for the pol. Capacitors around the LDO's

removed the I2C GPIO device

connected the power enable of the positive and negative LDO's ( removed one resistor to ground)

– added resistors to get the board also working without control

removed the temperatured alert

-- input for digital card or temperature is monitored via the I2C ??

amplifier

corrected the DC shifter. Connections where wrong ,

calculated resistor values for the level shifter added to the schematc .

removed the parallel capacitors at the input .

bias

R17 ( HV bias) will be placed by default. HV range increase by .5 V

added the GPIO connected GPIO to specific functions , 1 GPIO still not assigned

To do :

oct 06

added some capacitor.

rename input / output nets to be compatible with digital board

rename trim voltage signals to the i/o name so all should be consistent module D0 , ip0 , in0, trim0 ,op0 on0

Jan 2017

improvements / corrections

- fuses are to close to the connector so hard to replace (corrected inV1.3 )
- need a jumper on the power on line to power the board if no ADC board is connected.
  - also a 1.8 input or resistors from the 5 V.
- silkstreen W.Beaumont and Universiteit Antwerpen are not on the bottom silk screen( corrected layout V1.3 )
- LDAC and eeprom address lines to a socket so easy to connect. (done V 1.3)
- Solder resist mask DIN 61412 are not correct.( corrected in layout V1.3 )
- Added at input and output scotky diodes .on the power ( in V1.3 )
- added zener diode on the 1.8 V input ( done V1.3)
- added protection diodes between 1.8 and 0 V to protect ADC inputs ( done V1.3 , layout not done )
- put back ( ver 1.2) the connections of the input according the quotation version ( what was finally produced) done v1.3

20170327

Increase of the isolation for the HV lines

>>>>>>>>>>>

A sharp needlepoint will direct arc over at 1/3 the voltage of a rounded sphere. Example: for a 15

KV circuit, a 25 cm sphere will arc over at a spacing of .42, whereas a 2.5 cm sphere arc over

value is only increased to .48 cm, a sharp needlepoint will need 1.3 cm spacing. At the constant

spacing of .42 cm a needle will arc at 5 KV, a sphere at 15 KV.

<<<<<<<<<<<

spacing in the boards now is 0.15mm whould hold 115 V . If we follow the needle example == 119V/mm what comes close to 1kV /cm what is mostly used as rule of dump.

Still it is possible to increase the isolation to 20mm ( 8mill) .

Defined a net class 1 HV with as requirement isolation 8mill for all the HV lines ( before after the fuse and VBIAS

Added opto coupler for switch in HV circuit not tested yet. With resistor to bridge it in case it will not be used.

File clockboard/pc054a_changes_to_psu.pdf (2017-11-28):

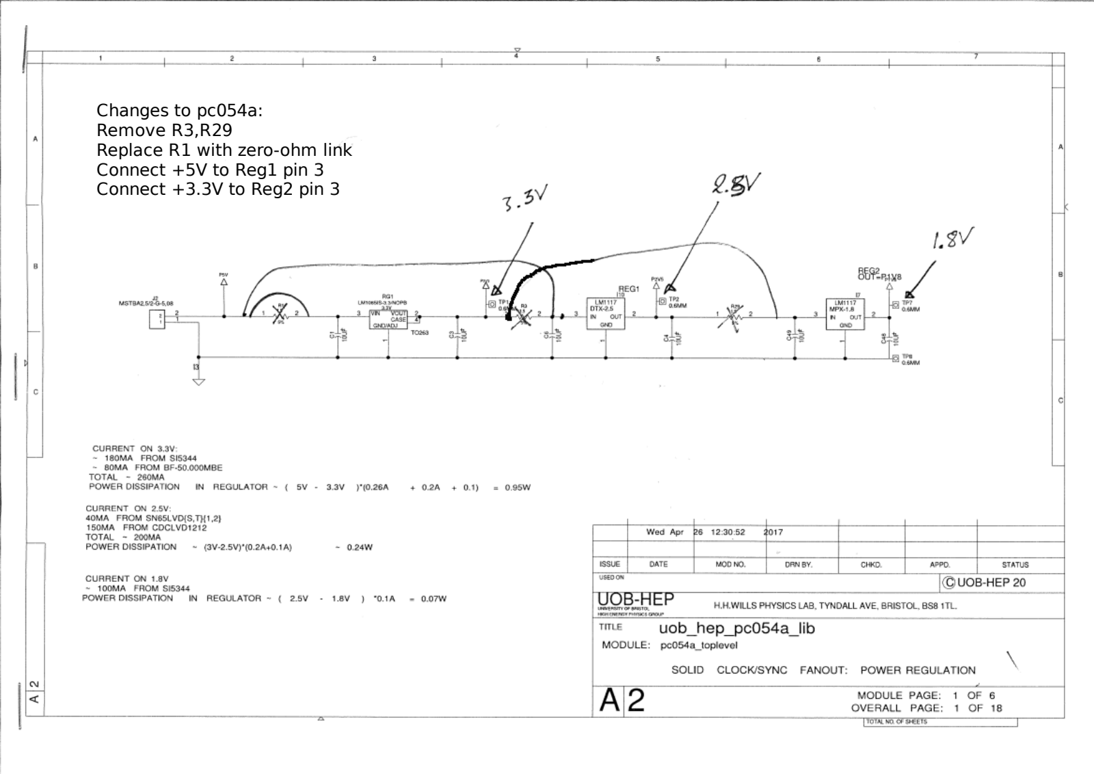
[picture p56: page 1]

Changes to pc054a:
Remove R3,R29
Replace R1 with zero-ohm link Connect +5V to Reg1 pin 3
Connect +3.3V to Reg2 pin 3

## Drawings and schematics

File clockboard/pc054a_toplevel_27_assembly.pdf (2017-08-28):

# A3-TE-

# University of Bristol HEP PROJECTION

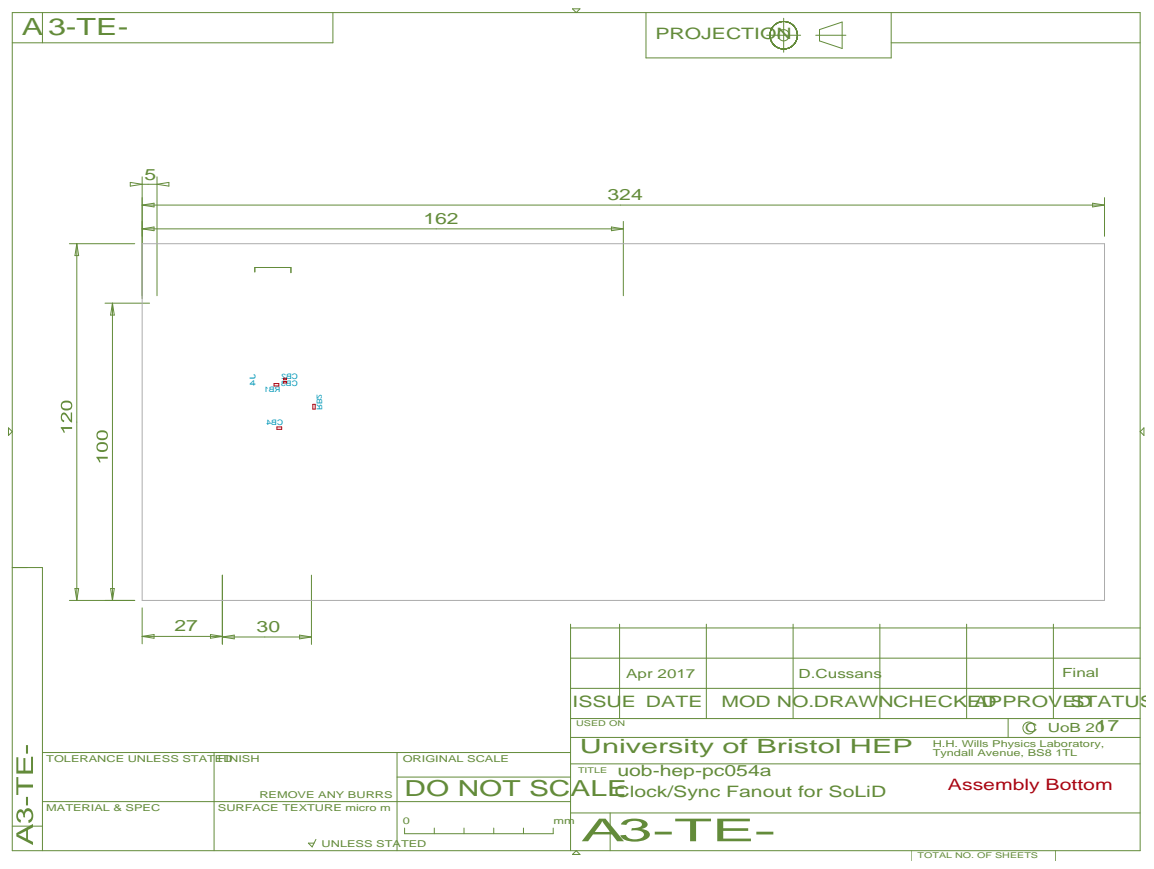
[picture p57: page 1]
ISSUE DATE; MOD NO.DRAWNCHECKEDAPPROVEDSTATUS; Apr 2017; D.Cussans; Final; MATERIAL & SPEC; FINISH; UNLESS STATED; TITLE; USED ON; C UoB 20

H.H. Wills Physics Laboratory,
Tyndall Avenue, BS8 1TL
Assembly Bottom

TOLERANCE UNLESS STATED

ORIGINAL SCALE
DO NOT SCALE

uob-hep-pc054a
Clock/Sync Fanout for SoLiD

REMOVE ANY BURRS

SURFACE TEXTURE micro m

TOTAL NO. OF SHEETS

# A3-TE-

# University of Bristol HEP PROJECTION

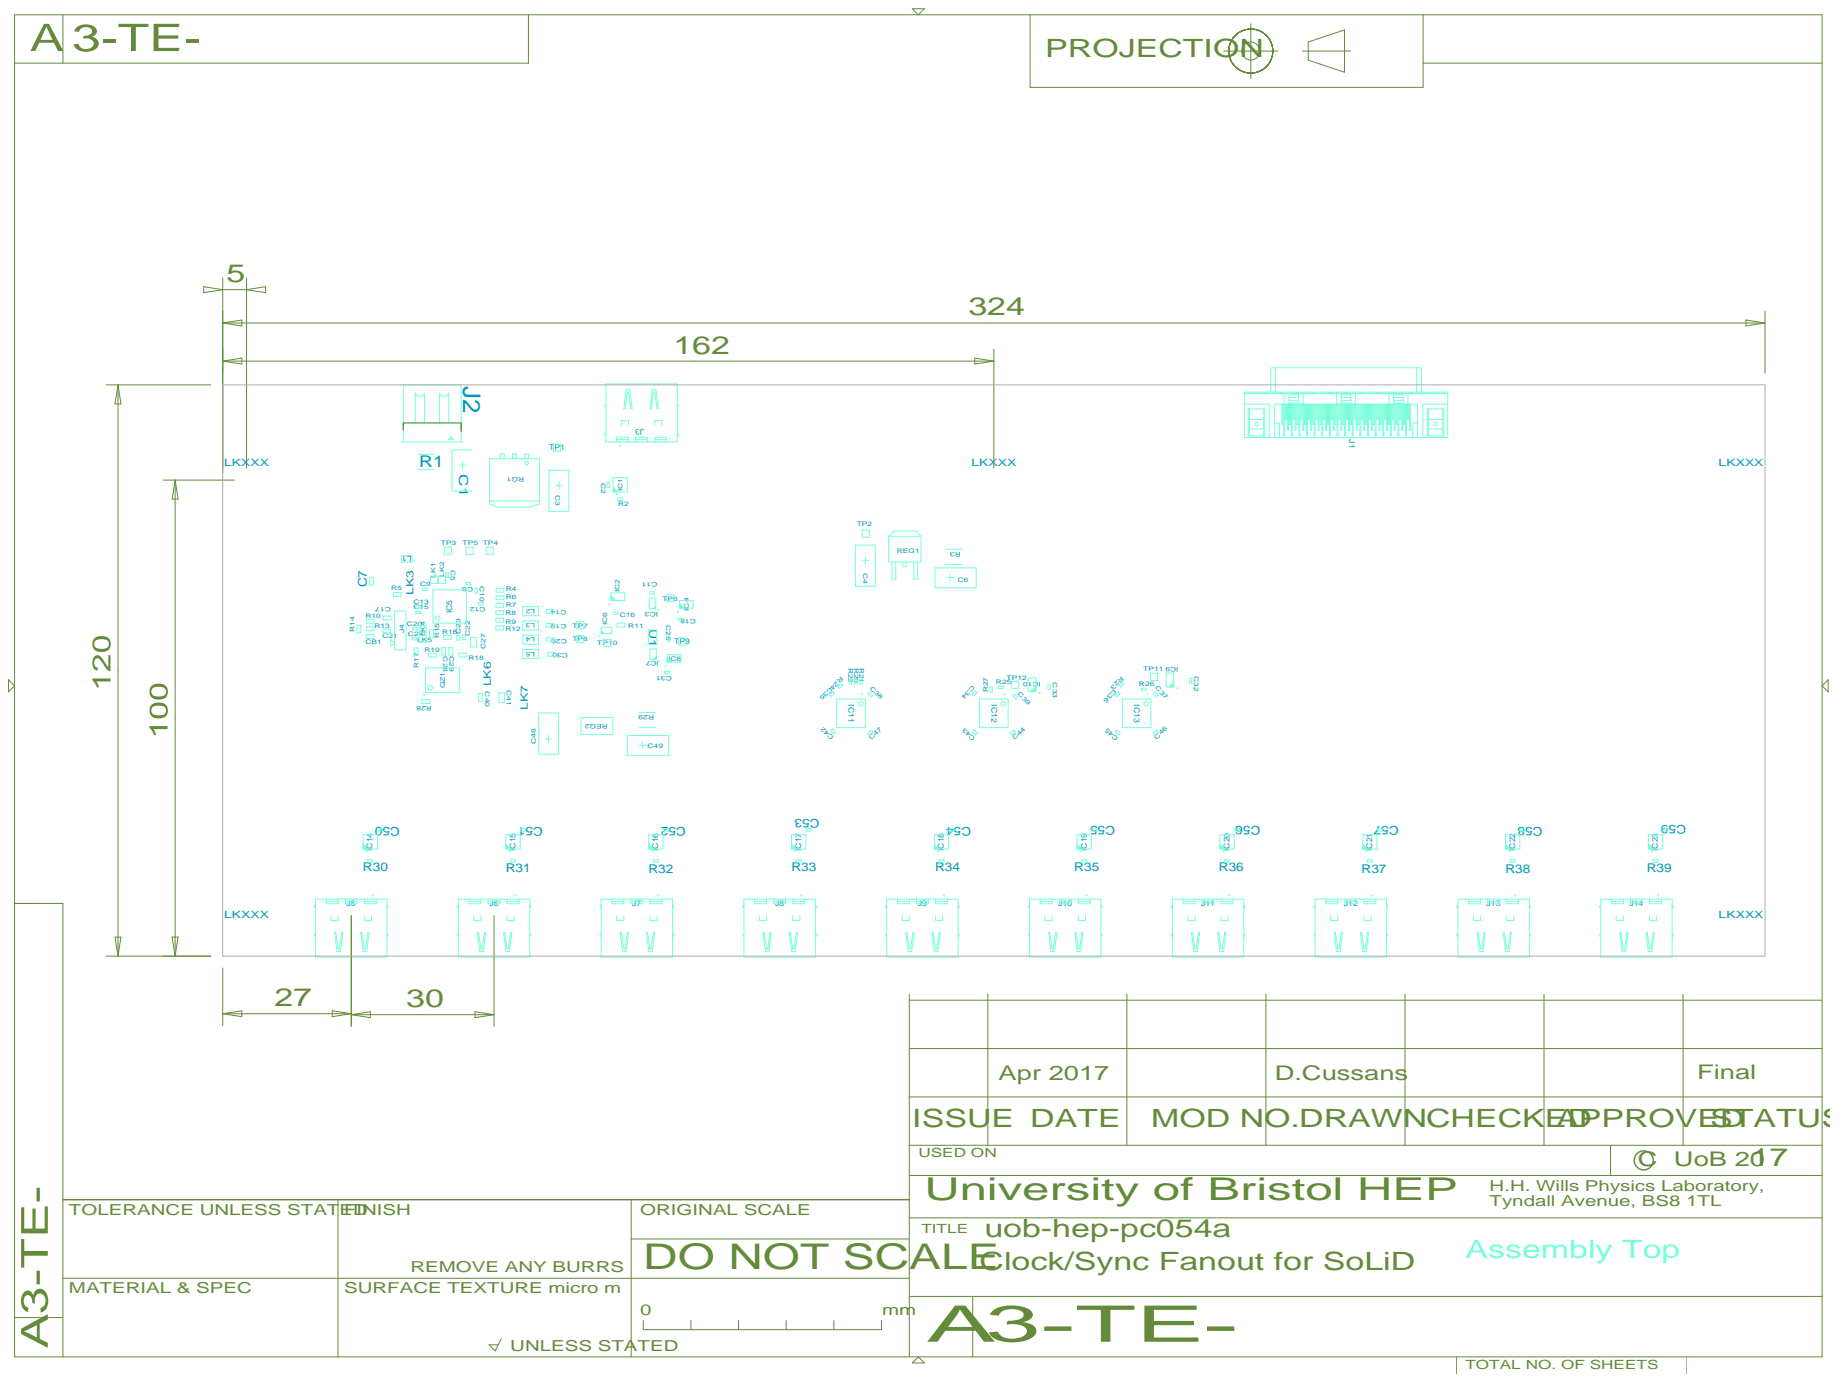
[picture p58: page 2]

uob-hep-pc054a
Clock/Sync Fanout for SoLiD

TOTAL NO. OF SHEETS

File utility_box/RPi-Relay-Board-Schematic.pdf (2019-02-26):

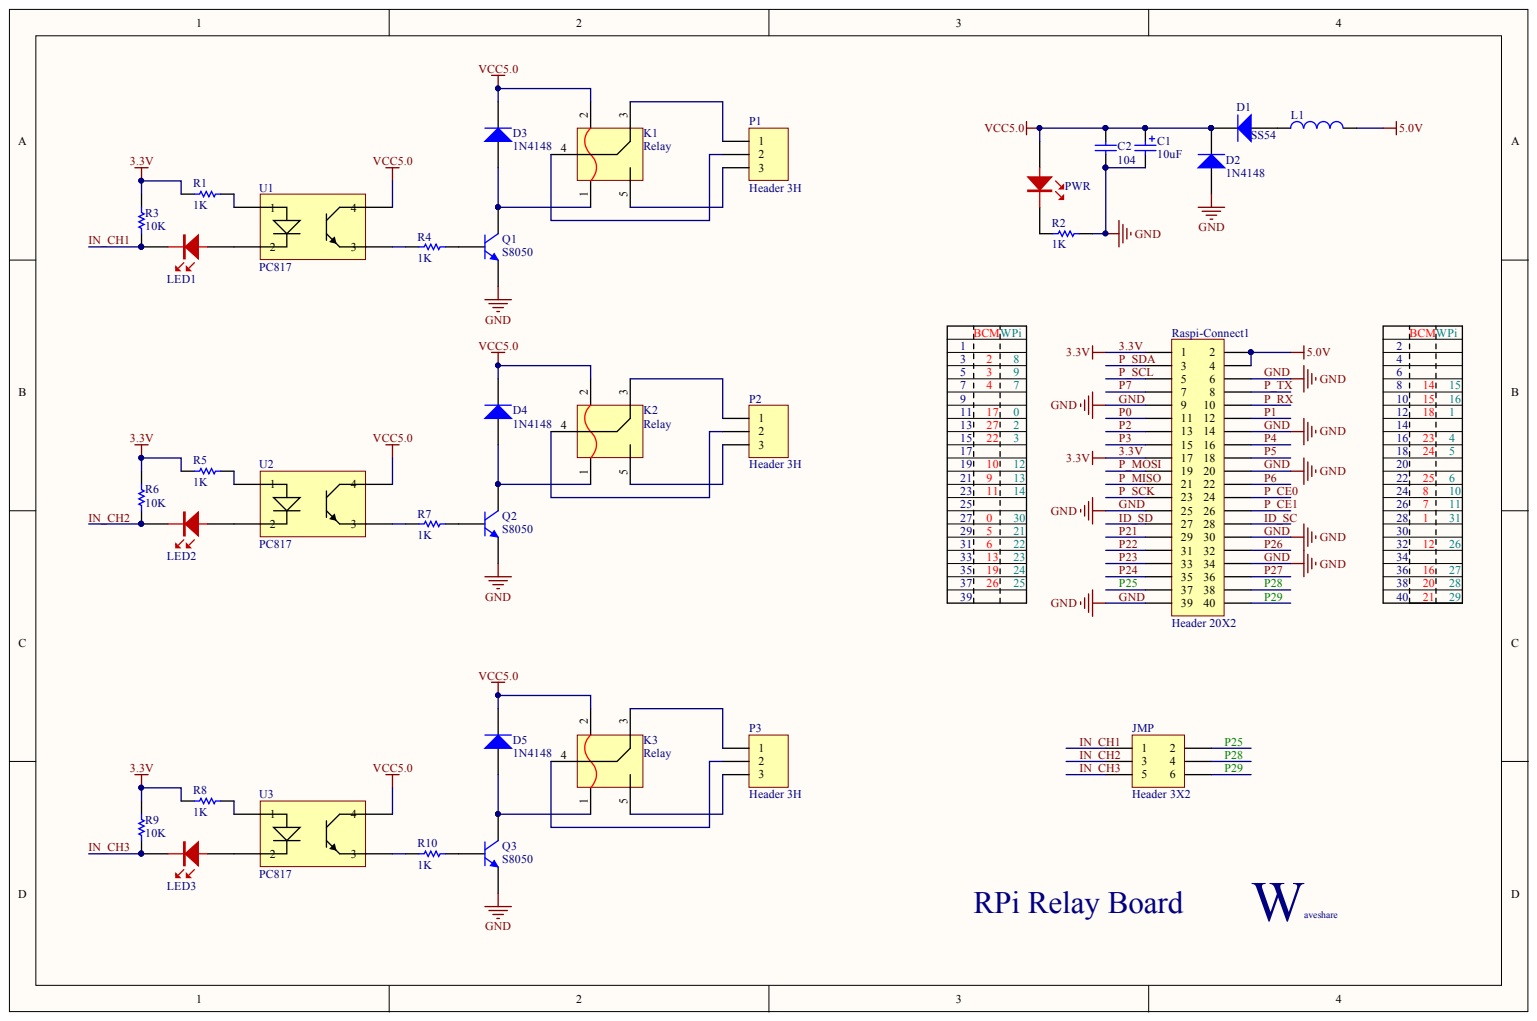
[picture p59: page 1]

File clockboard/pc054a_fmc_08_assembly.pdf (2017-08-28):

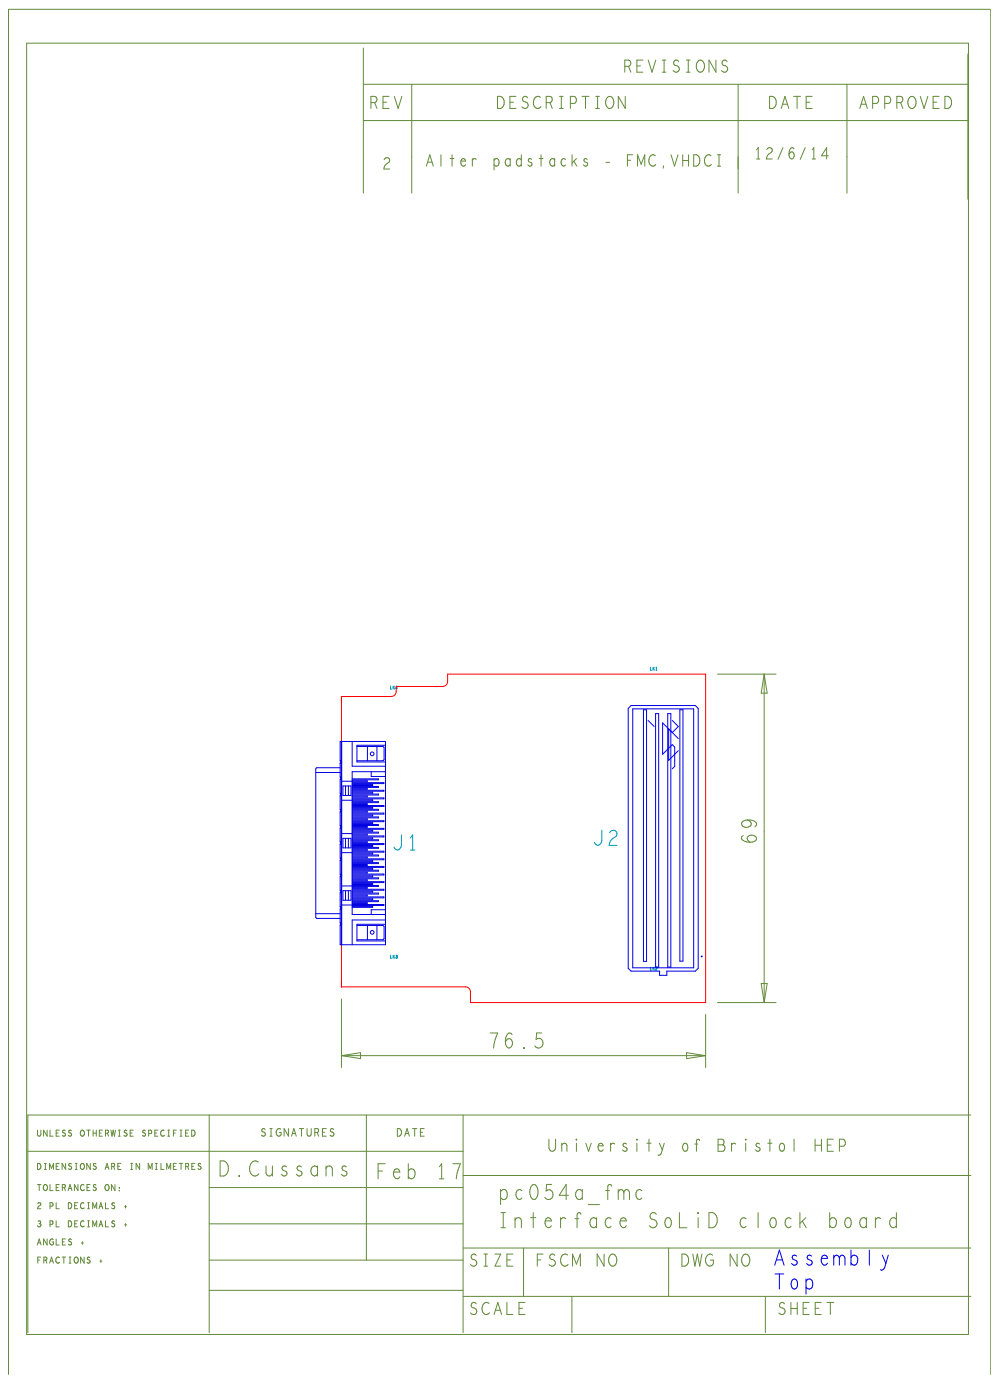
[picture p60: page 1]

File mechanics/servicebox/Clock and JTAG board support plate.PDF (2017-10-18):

7 98 11

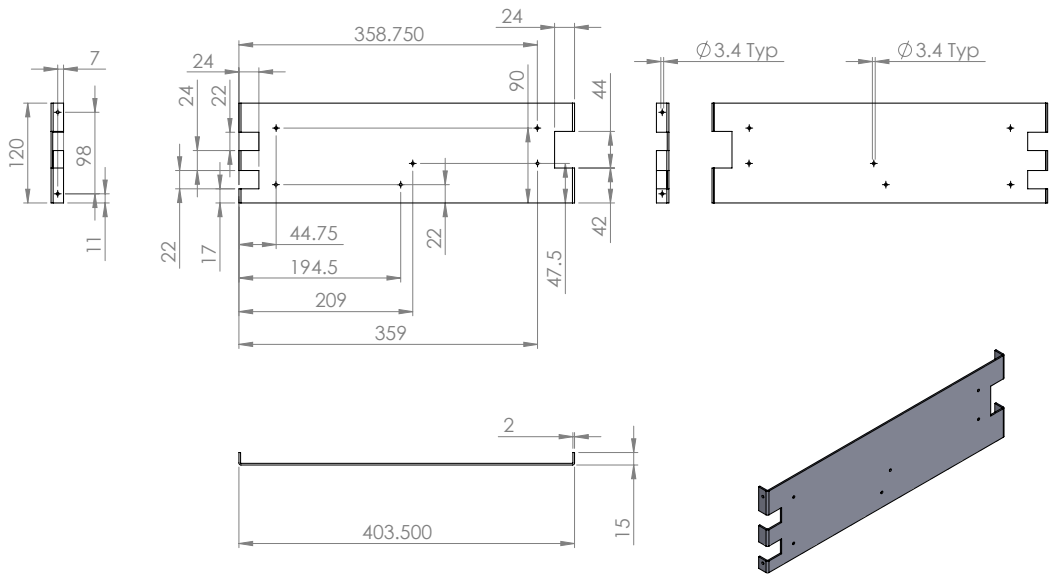
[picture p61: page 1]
3.4 Typ

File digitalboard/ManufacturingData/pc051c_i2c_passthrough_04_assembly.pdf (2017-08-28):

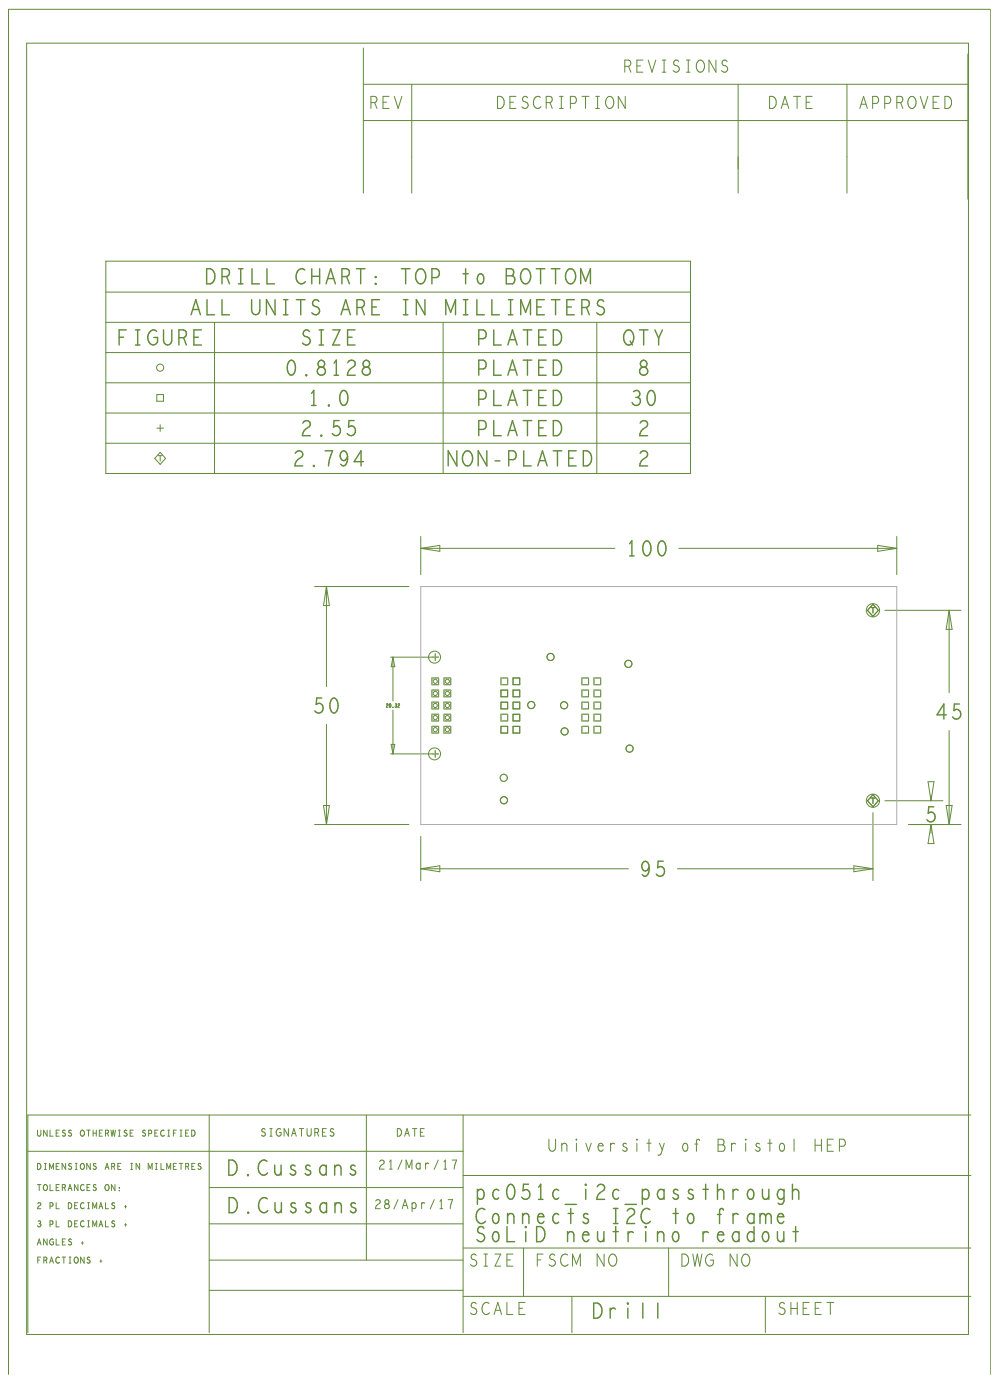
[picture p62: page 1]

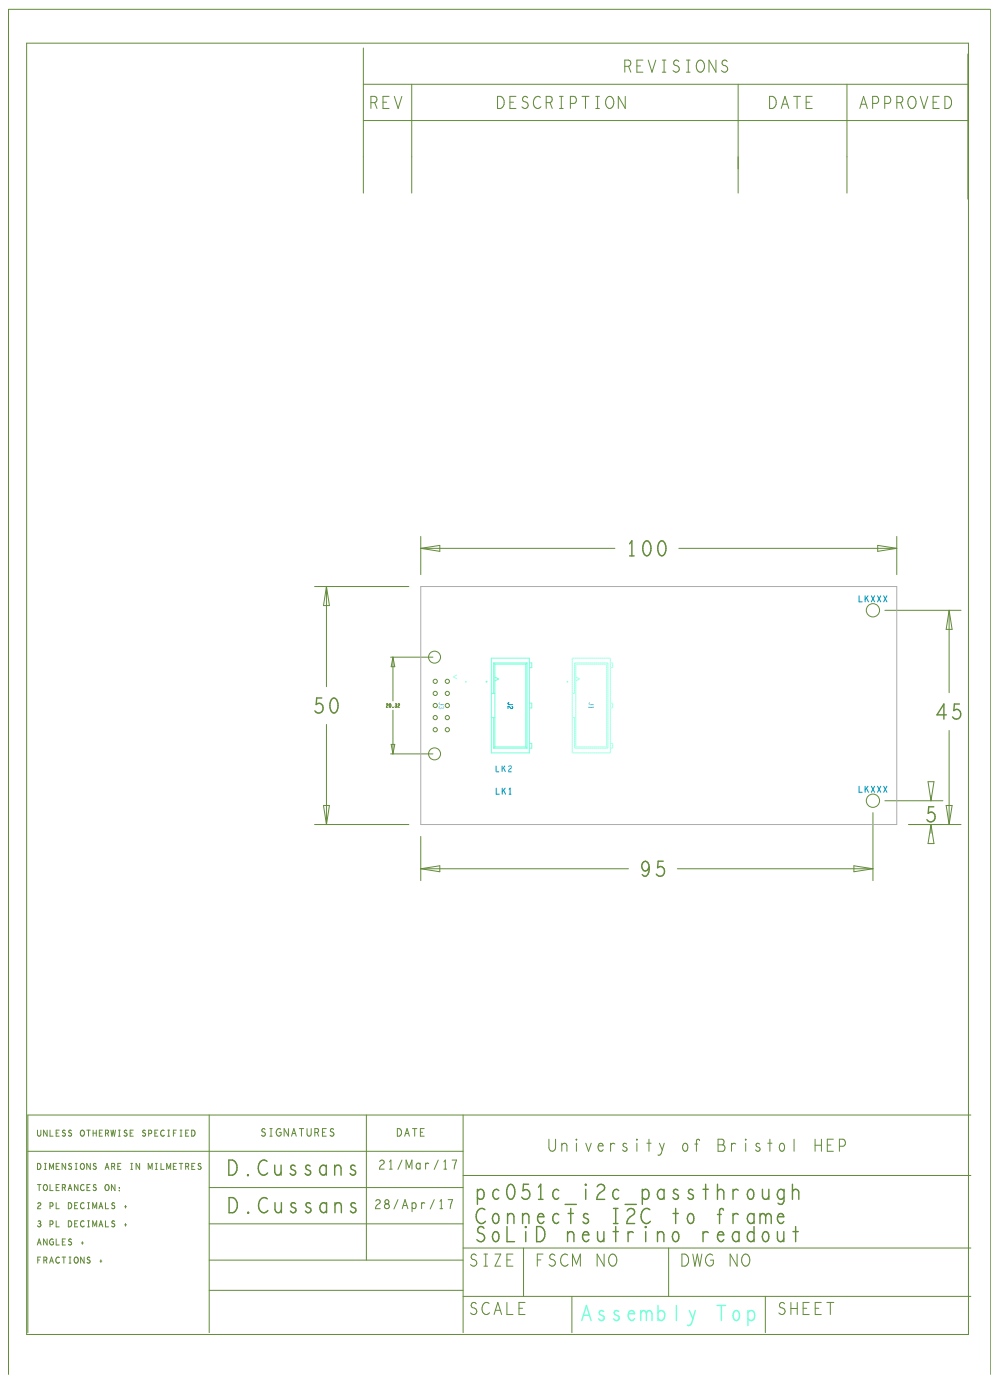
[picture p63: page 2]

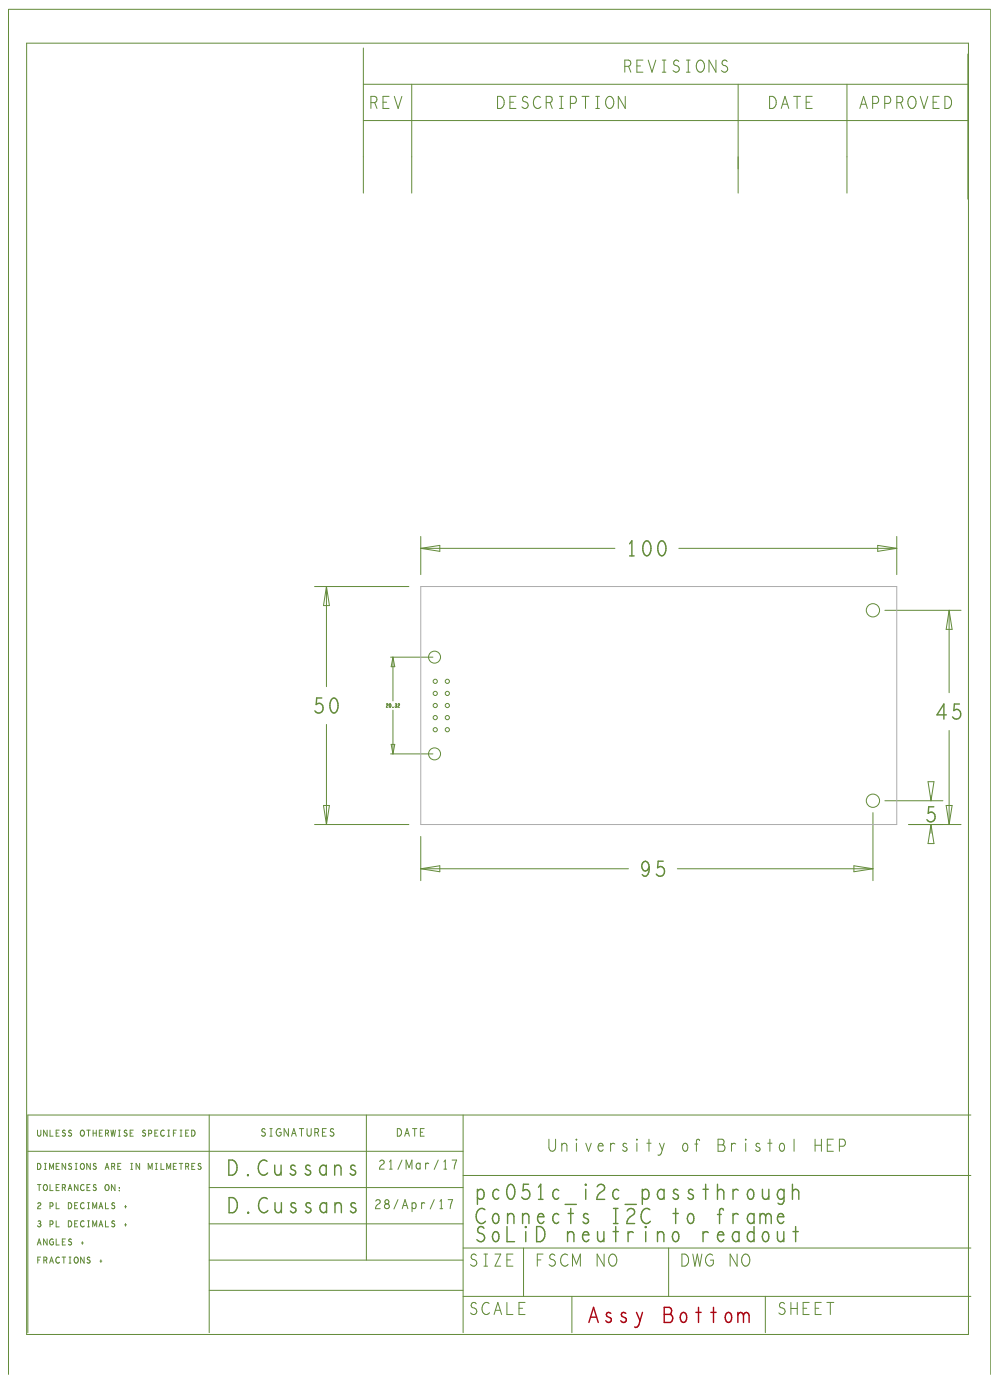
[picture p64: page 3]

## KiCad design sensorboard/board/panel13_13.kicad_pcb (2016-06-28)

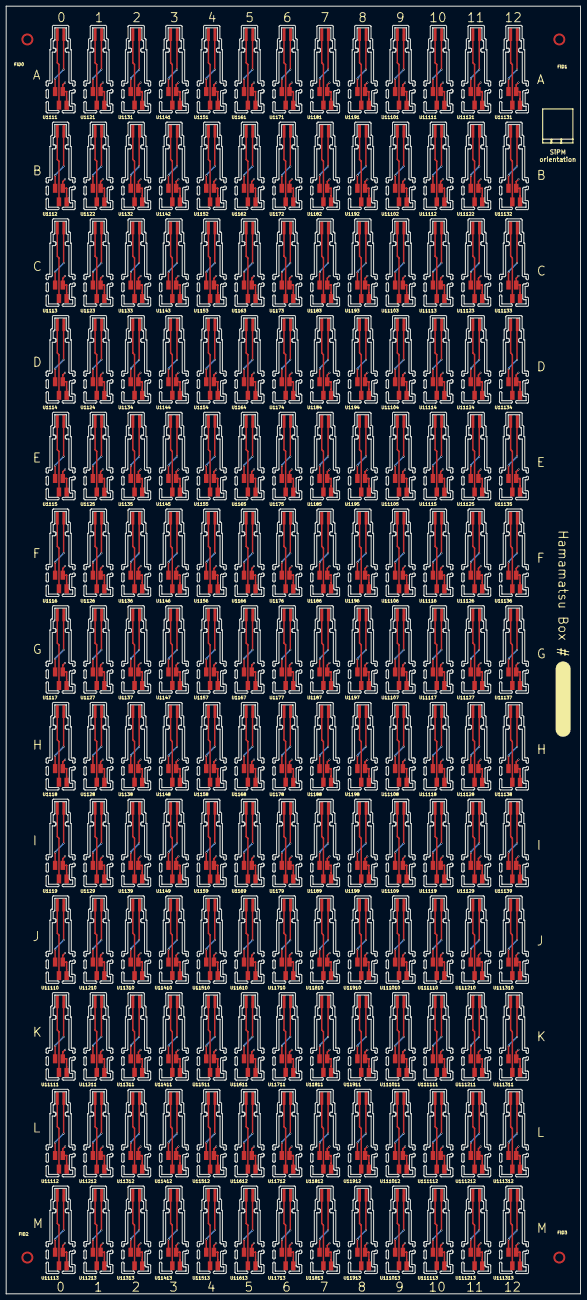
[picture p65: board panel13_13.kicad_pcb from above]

Board: 2 copper layers, 190.0 x 426.0 mm, 173 parts (0 on the bottom side), 3 nets.

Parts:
FID0, FID1, FID2, FID3: Fiducial_Modern_CopperTop
U1111, U1112, U1113, U1114, U1115, U1116, U1117, U1118, U1119, U1121, U1122, U1123, U1124, U1125, U1126, U1127, U1128, U1129, U1131, U1132, U1133, U1134, U1135, U1136, U1137, U1138, U1139, U1141, U1142, U1143, U1144, U1145, U1146, U1147, U1148, U1149, U1151, U1152, U1153, U1154, U1155, U1156, U1157, U1158, U1159, U1161, U1162, U1163, U1164, U1165, U1166, U1167, U1168, U1169, U1171, U1172, U1173, U1174, U1175, U1176, U1177, U1178, U1179, U1181, U1182, U1183, U1184, U1185, U1186, U1187, U1188, U1189, U1191, U1192, U1193, U1194, U1195, U1196, U1197, U1198, U1199, U11101, U11102, U11103, U11104, U11105, U11106, U11107, U11108, U11109, U11110, U11111, U11111#2, U11112, U11112#2, U11113, U11113#2, U11114, U11115, U11116, U11117, U11118, U11119, U11121, U11122, U11123, U11124, U11125, U11126, U11127, U11128, U11129, U11131, U11132, U11133, U11134, U11135, U11136, U11137, U11138, U11139, U11210, U11211, U11212, U11213, U11310, U11311, U11312, U11313, U11410, U11411, U11412, U11413, U11510, U11511, U11512, U11513, U11610, U11611, U11612, U11613, U11710, U11711, U11712, U11713, U11810, U11811, U11812, U11813, U11910, U11911, U11912, U11913, U111010, U111011, U111012, U111013, U111110, U111111, U111112, U111113, U111210, U111211, U111212, U111213, U111310, U111311, U111312, U111313: SiPM_Socket; sipm_socket

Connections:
GND: U1111.1, U1111.2, U1112.1, U1112.2, U1113.1, U1113.2, U1114.1, U1114.2, U1115.1, U1115.2, U1116.1, U1116.2, U1117.1, U1117.2, U1118.1, U1118.2, U1119.1, U1119.2, U1121.1, U1121.2, U1122.1, U1122.2, U1123.1, U1123.2, U1124.1, U1124.2, U1125.1, U1125.2, U1126.1, U1126.2, U1127.1, U1127.2, U1128.1, U1128.2, U1129.1, U1129.2, U1131.1, U1131.2, U1132.1, U1132.2, U1133.1, U1133.2, U1134.1, U1134.2, U1135.1, U1135.2, U1136.1, U1136.2, U1137.1, U1137.2, U1138.1, U1138.2, U1139.1, U1139.2, U1141.1, U1141.2, U1142.1, U1142.2, U1143.1, U1143.2, U1144.1, U1144.2, U1145.1, U1145.2, U1146.1, U1146.2, U1147.1, U1147.2, U1148.1, U1148.2, U1149.1, U1149.2, U1151.1, U1151.2, U1152.1, U1152.2, U1153.1, U1153.2, U1154.1, U1154.2, U1155.1, U1155.2, U1156.1, U1156.2, U1157.1, U1157.2, U1158.1, U1158.2, U1159.1, U1159.2, U1161.1, U1161.2, U1162.1, U1162.2, U1163.1, U1163.2, U1164.1, U1164.2, U1165.1, U1165.2, U1166.1, U1166.2, U1167.1, U1167.2, U1168.1, U1168.2, U1169.1, U1169.2, U1171.1, U1171.2, U1172.1, U1172.2, U1173.1, U1173.2, U1174.1, U1174.2, U1175.1, U1175.2, U1176.1, U1176.2, U1177.1, U1177.2, U1178.1, U1178.2, U1179.1, U1179.2, U1181.1, U1181.2, U1182.1, U1182.2, U1183.1, U1183.2, U1184.1, U1184.2, U1185.1, U1185.2, U1186.1, U1186.2, U1187.1, U1187.2, U1188.1, U1188.2, U1189.1, U1189.2, U1191.1, U1191.2, U1192.1, U1192.2, U1193.1, U1193.2, U1194.1, U1194.2, U1195.1, U1195.2, U1196.1, U1196.2, U1197.1, U1197.2, U1198.1, U1198.2, U1199.1, U1199.2, U11101.1, U11101.2, U11102.1, U11102.2, U11103.1, U11103.2, U11104.1, U11104.2, U11105.1, U11105.2, U11106.1, U11106.2, U11107.1, U11107.2, U11108.1, U11108.2, U11109.1, U11109.2, U11110.1, U11110.2, U11111.1, U11111.2, U11111#2.1, U11111#2.2, U11112.1, U11112.2, U11112#2.1, U11112#2.2, U11113.1, U11113.2, U11113#2.1, U11113#2.2, U11114.1, U11114.2, U11115.1, U11115.2, U11116.1, U11116.2, U11117.1, U11117.2, U11118.1, U11118.2, U11119.1, U11119.2, U11121.1, U11121.2, U11122.1, U11122.2, U11123.1, U11123.2, U11124.1, U11124.2, U11125.1, U11125.2, U11126.1, U11126.2, U11127.1, U11127.2, U11128.1, U11128.2, U11129.1, U11129.2, U11131.1, U11131.2, U11132.1, U11132.2, U11133.1, U11133.2, U11134.1, U11134.2, U11135.1, U11135.2, U11136.1, U11136.2, U11137.1, U11137.2, U11138.1, U11138.2, U11139.1, U11139.2, U11210.1, U11210.2, U11211.1, U11211.2, U11212.1, U11212.2, U11213.1, U11213.2, U11310.1, U11310.2, U11311.1, U11311.2, U11312.1, U11312.2, U11313.1, U11313.2, U11410.1, U11410.2, U11411.1, U11411.2, U11412.1, U11412.2, U11413.1, U11413.2, U11510.1, U11510.2, U11511.1, U11511.2, U11512.1, U11512.2, U11513.1, U11513.2, U11610.1, U11610.2, U11611.1, U11611.2, U11612.1, U11612.2, U11613.1, U11613.2, U11710.1, U11710.2, U11711.1, U11711.2, U11712.1, U11712.2, U11713.1, U11713.2, U11810.1, U11810.2, U11811.1, U11811.2, U11812.1, U11812.2, U11813.1, U11813.2, U11910.1, U11910.2, U11911.1, U11911.2, U11912.1, U11912.2, U11913.1, U11913.2, U111010.1, U111010.2, U111011.1, U111011.2, U111012.1, U111012.2, U111013.1, U111013.2, U111110.1, U111110.2, U111111.1, U111111.2, U111112.1, U111112.2, U111113.1, U111113.2, U111210.1, U111210.2, U111211.1, U111211.2, U111212.1, U111212.2, U111213.1, U111213.2, U111310.1, U111310.2, U111311.1, U111311.2, U111312.1, U111312.2, U111313.1, U111313.2
unnamed: U1111.3, U1111.6, U1112.3, U1112.6, U1113.3, U1113.6, U1114.3, U1114.6, U1115.3, U1115.6, U1116.3, U1116.6, U1117.3, U1117.6, U1118.3, U1118.6, U1119.3, U1119.6, U1121.3, U1121.6, U1122.3, U1122.6, U1123.3, U1123.6, U1124.3, U1124.6, U1125.3, U1125.6, U1126.3, U1126.6, U1127.3, U1127.6, U1128.3, U1128.6, U1129.3, U1129.6, U1131.3, U1131.6, U1132.3, U1132.6, U1133.3, U1133.6, U1134.3, U1134.6, U1135.3, U1135.6, U1136.3, U1136.6, U1137.3, U1137.6, U1138.3, U1138.6, U1139.3, U1139.6, U1141.3, U1141.6, U1142.3, U1142.6, U1143.3, U1143.6, U1144.3, U1144.6, U1145.3, U1145.6, U1146.3, U1146.6, U1147.3, U1147.6, U1148.3, U1148.6, U1149.3, U1149.6, U1151.3, U1151.6, U1152.3, U1152.6, U1153.3, U1153.6, U1154.3, U1154.6, U1155.3, U1155.6, U1156.3, U1156.6, U1157.3, U1157.6, U1158.3, U1158.6, U1159.3, U1159.6, U1161.3, U1161.6, U1162.3, U1162.6, U1163.3, U1163.6, U1164.3, U1164.6, U1165.3, U1165.6, U1166.3, U1166.6, U1167.3, U1167.6, U1168.3, U1168.6, U1169.3, U1169.6, U1171.3, U1171.6, U1172.3, U1172.6, U1173.3, U1173.6, U1174.3, U1174.6, U1175.3, U1175.6, U1176.3, U1176.6, U1177.3, U1177.6, U1178.3, U1178.6, U1179.3, U1179.6, U1181.3, U1181.6, U1182.3, U1182.6, U1183.3, U1183.6, U1184.3, U1184.6, U1185.3, U1185.6, U1186.3, U1186.6, U1187.3, U1187.6, U1188.3, U1188.6, U1189.3, U1189.6, U1191.3, U1191.6, U1192.3, U1192.6, U1193.3, U1193.6, U1194.3, U1194.6, U1195.3, U1195.6, U1196.3, U1196.6, U1197.3, U1197.6, U1198.3, U1198.6, U1199.3, U1199.6, U11101.3, U11101.6, U11102.3, U11102.6, U11103.3, U11103.6, U11104.3, U11104.6, U11105.3, U11105.6, U11106.3, U11106.6, U11107.3, U11107.6, U11108.3, U11108.6, U11109.3, U11109.6, U11110.3, U11110.6, U11111.3, U11111.6, U11111#2.3, U11111#2.6, U11112.3, U11112.6, U11112#2.3, U11112#2.6, U11113.3, U11113.6, U11113#2.3, U11113#2.6, U11114.3, U11114.6, U11115.3, U11115.6, U11116.3, U11116.6, U11117.3, U11117.6, U11118.3, U11118.6, U11119.3, U11119.6, U11121.3, U11121.6, U11122.3, U11122.6, U11123.3, U11123.6, U11124.3, U11124.6, U11125.3, U11125.6, U11126.3, U11126.6, U11127.3, U11127.6, U11128.3, U11128.6, U11129.3, U11129.6, U11131.3, U11131.6, U11132.3, U11132.6, U11133.3, U11133.6, U11134.3, U11134.6, U11135.3, U11135.6, U11136.3, U11136.6, U11137.3, U11137.6, U11138.3, U11138.6, U11139.3, U11139.6, U11210.3, U11210.6, U11211.3, U11211.6, U11212.3, U11212.6, U11213.3, U11213.6, U11310.3, U11310.6, U11311.3, U11311.6, U11312.3, U11312.6, U11313.3, U11313.6, U11410.3, U11410.6, U11411.3, U11411.6, U11412.3, U11412.6, U11413.3, U11413.6, U11510.3, U11510.6, U11511.3, U11511.6, U11512.3, U11512.6, U11513.3, U11513.6, U11610.3, U11610.6, U11611.3, U11611.6, U11612.3, U11612.6, U11613.3, U11613.6, U11710.3, U11710.6, U11711.3, U11711.6, U11712.3, U11712.6, U11713.3, U11713.6, U11810.3, U11810.6, U11811.3, U11811.6, U11812.3, U11812.6, U11813.3, U11813.6, U11910.3, U11910.6, U11911.3, U11911.6, U11912.3, U11912.6, U11913.3, U11913.6, U111010.3, U111010.6, U111011.3, U111011.6, U111012.3, U111012.6, U111013.3, U111013.6, U111110.3, U111110.6, U111111.3, U111111.6, U111112.3, U111112.6, U111113.3, U111113.6, U111210.3, U111210.6, U111211.3, U111211.6, U111212.3, U111212.6, U111213.3, U111213.6, U111310.3, U111310.6, U111311.3, U111311.6, U111312.3, U111312.6, U111313.3, U111313.6
unnamed: U1111.4, U1111.5, U1112.4, U1112.5, U1113.4, U1113.5, U1114.4, U1114.5, U1115.4, U1115.5, U1116.4, U1116.5, U1117.4, U1117.5, U1118.4, U1118.5, U1119.4, U1119.5, U1121.4, U1121.5, U1122.4, U1122.5, U1123.4, U1123.5, U1124.4, U1124.5, U1125.4, U1125.5, U1126.4, U1126.5, U1127.4, U1127.5, U1128.4, U1128.5, U1129.4, U1129.5, U1131.4, U1131.5, U1132.4, U1132.5, U1133.4, U1133.5, U1134.4, U1134.5, U1135.4, U1135.5, U1136.4, U1136.5, U1137.4, U1137.5, U1138.4, U1138.5, U1139.4, U1139.5, U1141.4, U1141.5, U1142.4, U1142.5, U1143.4, U1143.5, U1144.4, U1144.5, U1145.4, U1145.5, U1146.4, U1146.5, U1147.4, U1147.5, U1148.4, U1148.5, U1149.4, U1149.5, U1151.4, U1151.5, U1152.4, U1152.5, U1153.4, U1153.5, U1154.4, U1154.5, U1155.4, U1155.5, U1156.4, U1156.5, U1157.4, U1157.5, U1158.4, U1158.5, U1159.4, U1159.5, U1161.4, U1161.5, U1162.4, U1162.5, U1163.4, U1163.5, U1164.4, U1164.5, U1165.4, U1165.5, U1166.4, U1166.5, U1167.4, U1167.5, U1168.4, U1168.5, U1169.4, U1169.5, U1171.4, U1171.5, U1172.4, U1172.5, U1173.4, U1173.5, U1174.4, U1174.5, U1175.4, U1175.5, U1176.4, U1176.5, U1177.4, U1177.5, U1178.4, U1178.5, U1179.4, U1179.5, U1181.4, U1181.5, U1182.4, U1182.5, U1183.4, U1183.5, U1184.4, U1184.5, U1185.4, U1185.5, U1186.4, U1186.5, U1187.4, U1187.5, U1188.4, U1188.5, U1189.4, U1189.5, U1191.4, U1191.5, U1192.4, U1192.5, U1193.4, U1193.5, U1194.4, U1194.5, U1195.4, U1195.5, U1196.4, U1196.5, U1197.4, U1197.5, U1198.4, U1198.5, U1199.4, U1199.5, U11101.4, U11101.5, U11102.4, U11102.5, U11103.4, U11103.5, U11104.4, U11104.5, U11105.4, U11105.5, U11106.4, U11106.5, U11107.4, U11107.5, U11108.4, U11108.5, U11109.4, U11109.5, U11110.4, U11110.5, U11111.4, U11111.5, U11111#2.4, U11111#2.5, U11112.4, U11112.5, U11112#2.4, U11112#2.5, U11113.4, U11113.5, U11113#2.4, U11113#2.5, U11114.4, U11114.5, U11115.4, U11115.5, U11116.4, U11116.5, U11117.4, U11117.5, U11118.4, U11118.5, U11119.4, U11119.5, U11121.4, U11121.5, U11122.4, U11122.5, U11123.4, U11123.5, U11124.4, U11124.5, U11125.4, U11125.5, U11126.4, U11126.5, U11127.4, U11127.5, U11128.4, U11128.5, U11129.4, U11129.5, U11131.4, U11131.5, U11132.4, U11132.5, U11133.4, U11133.5, U11134.4, U11134.5, U11135.4, U11135.5, U11136.4, U11136.5, U11137.4, U11137.5, U11138.4, U11138.5, U11139.4, U11139.5, U11210.4, U11210.5, U11211.4, U11211.5, U11212.4, U11212.5, U11213.4, U11213.5, U11310.4, U11310.5, U11311.4, U11311.5, U11312.4, U11312.5, U11313.4, U11313.5, U11410.4, U11410.5, U11411.4, U11411.5, U11412.4, U11412.5, U11413.4, U11413.5, U11510.4, U11510.5, U11511.4, U11511.5, U11512.4, U11512.5, U11513.4, U11513.5, U11610.4, U11610.5, U11611.4, U11611.5, U11612.4, U11612.5, U11613.4, U11613.5, U11710.4, U11710.5, U11711.4, U11711.5, U11712.4, U11712.5, U11713.4, U11713.5, U11810.4, U11810.5, U11811.4, U11811.5, U11812.4, U11812.5, U11813.4, U11813.5, U11910.4, U11910.5, U11911.4, U11911.5, U11912.4, U11912.5, U11913.4, U11913.5, U111010.4, U111010.5, U111011.4, U111011.5, U111012.4, U111012.5, U111013.4, U111013.5, U111110.4, U111110.5, U111111.4, U111111.5, U111112.4, U111112.5, U111113.4, U111113.5, U111210.4, U111210.5, U111211.4, U111211.5, U111212.4, U111212.5, U111213.4, U111213.5, U111310.4, U111310.5, U111311.4, U111311.5, U111312.4, U111312.5, U111313.4, U111313.5

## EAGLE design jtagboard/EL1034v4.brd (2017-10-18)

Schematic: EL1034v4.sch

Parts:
C1, C4, C36: 100u; EIA7343
C2, C3, C5, C6, C7, C8, C9, C10, C11, C12, C13, C14, C15, C16, C17, C18, C19, C20, C21, C22, C23, C24, C25, C26, C27, C28, C29, C30, C31, C32, C33, C34, C35, C37: 100n; 0805
CON1: SL5.08/2
D1, D2, D3, D4, D5, D6, D7, D8, D9: RED; LED-0603
HDMI0, HDMI1, HDMI2, HDMI3, HDMI4, HDMI5, HDMI6, HDMI7, HDMI8, HDMI9: 47266-0001
IC1, IC3, IC5, IC7, IC9, IC11, IC13, IC15, IC17, IC19: DS90LV031ATMX; SOIC127P600X175-16N
IC2, IC4, IC6, IC8, IC10, IC12, IC14, IC16, IC18, IC20: SN65LVDT2DBVT; SOT95P280X145-5N
IC21, IC22, IC23, IC24, IC25, IC26, IC27, IC28: 74LV4051PW; TSSOP16
IC29: LM3940; TO220-IGO
IC30: 74LVC1G14SE-7; SOT65P210X110-5N
JP1, JP2, JP3, JP4, JP5, JP6, JP7, JP8, JP9, JP10, JP11: M06POLAR; MOLEX-1X6
JP12, JP13: M02POLAR; MOLEX-1X2
MOD1: JTAG-SMT2; JTAG_SMT2
R1, R3, R5, R7, R9, R30, R32, R34, R36, R38, R40, R42, R44, R46, R48, R50, R52, R54, R56, R58, R60, R62, R64, R66, R68, R70, R72, R74, R76, R78: DNF; 0603-RES
R2, R4, R6, R8, R10, R31, R33, R35, R37, R39, R41, R43, R45, R47, R49, R51, R53, R55, R57, R59, R61, R63, R65, R67, R69, R71, R73, R75, R77, R79: 100k; 0603-RES
R11, R12, R13, R14, R15, R16, R17, R18, R19, R20: 10k; 0603-RES
R21, R22, R23, R24, R25, R26, R27, R28, R29: 2K2; 0603-RES
SJ1, SJ2, SJ3, SJ4, SJ5, SJ6, SJ7, SJ8, SJ9, SJ10, SJ11, SJ12, SJ13: SOLDERJUMPERNO; SJ_2S-NO
STANDOFF1, STANDOFF2, STANDOFF3, STANDOFF4, STANDOFF5, STANDOFF6, STANDOFF7: STAND-OFF
TP1, TP2: TEST-POINTTP_15TH_THRU; TP_15TH

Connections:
3.3V: C3.1, C4.A (+), C5.1, C6.1, C7.1, C8.1, C9.1, C10.1, C11.1, C12.1, C13.1, C14.2, C15.2, C16.2, C17.2, C18.2, C19.2, C20.2, C21.2, C22.2, C23.2, C24.2, C25.2, C26.2, C27.2, C28.2, C29.2, C30.2, C31.2, C32.2, C33.2, C34.2, C35.1, C36.A (+), C37.1, D9.A, IC1.4 (EN), IC1.16 (VCC), IC2.1 (VCC), IC3.4 (EN), IC3.16 (VCC), IC4.1 (VCC), IC5.4 (EN), IC5.16 (VCC), IC6.1 (VCC), IC7.4 (EN), IC7.16 (VCC), IC8.1 (VCC), IC9.4 (EN), IC9.16 (VCC), IC10.1 (VCC), IC11.4 (EN), IC11.16 (VCC), IC12.1 (VCC), IC13.4 (EN), IC13.16 (VCC), IC14.1 (VCC), IC15.4 (EN), IC15.16 (VCC), IC16.1 (VCC), IC17.4 (EN), IC17.16 (VCC), IC18.1 (VCC), IC19.4 (EN), IC19.16 (VCC), IC20.1 (VCC), IC21.16 (VCC), IC22.16 (VCC), IC23.16 (VCC), IC24.16 (VCC), IC25.16 (VCC), IC26.16 (VCC), IC27.16 (VCC), IC28.16 (VCC), IC29.OUT, IC30.5 (VCC), JP12.2, JP13.2, MOD1.9 (VREF), MOD1.11 (VDD), R1.2, R3.2, R5.2, R7.2, R9.2, R11.2, R12.2, R13.2, R14.2, R15.2, R16.2, R17.2, R18.2, R19.2, R20.2, R30.2, R32.2, R34.2, R36.2, R38.2, R40.2, R42.2, R44.2, R46.2, R48.2, R50.2, R52.2, R54.2, R56.2, R58.2, R60.2, R62.2, R64.2, R66.2, R68.2, R70.2, R72.2, R74.2, R76.2, R78.2, TP1.P$1
5V_IN: C1.A (+), C2.1, CON1.P$1, IC29.IN, JP1.2
!S3: IC22.6 (!E), IC24.6 (!E), IC26.6 (!E), IC28.6 (!E), IC30.4 (Y)
GND: C1.C (-), C2.2, C3.2, C4.C (-), C5.2, C6.2, C7.2, C8.2, C9.2, C10.2, C11.2, C12.2, C13.2, C14.1, C15.1, C16.1, C17.1, C18.1, C19.1, C20.1, C21.1, C22.1, C23.1, C24.1, C25.1, C26.1, C27.1, C28.1, C29.1, C30.1, C31.1, C32.1, C33.1, C34.1, C35.2, C36.C (-), C37.2, CON1.P$2, HDMI0.2, HDMI0.5, HDMI0.8, HDMI0.11, HDMI0.13, HDMI0.14, HDMI0.17, HDMI0.18, HDMI0.19, HDMI0.SHELL1, HDMI0.SHELL2, HDMI0.SHELL3, HDMI0.SHELL4, HDMI1.2, HDMI1.5, HDMI1.8, HDMI1.11, HDMI1.13, HDMI1.14, HDMI1.17, HDMI1.18, HDMI1.19, HDMI1.SHELL1, HDMI1.SHELL2, HDMI1.SHELL3, HDMI1.SHELL4, HDMI2.2, HDMI2.5, HDMI2.8, HDMI2.11, HDMI2.13, HDMI2.14, HDMI2.17, HDMI2.18, HDMI2.19, HDMI2.SHELL1, HDMI2.SHELL2, HDMI2.SHELL3, HDMI2.SHELL4, HDMI3.2, HDMI3.5, HDMI3.8, HDMI3.11, HDMI3.13, HDMI3.14, HDMI3.17, HDMI3.18, HDMI3.19, HDMI3.SHELL1, HDMI3.SHELL2, HDMI3.SHELL3, HDMI3.SHELL4, HDMI4.2, HDMI4.5, HDMI4.8, HDMI4.11, HDMI4.13, HDMI4.14, HDMI4.17, HDMI4.18, HDMI4.19, HDMI4.SHELL1, HDMI4.SHELL2, HDMI4.SHELL3, HDMI4.SHELL4, HDMI5.2, HDMI5.5, HDMI5.8, HDMI5.11, HDMI5.13, HDMI5.14, HDMI5.17, HDMI5.18, HDMI5.19, HDMI5.SHELL1, HDMI5.SHELL2, HDMI5.SHELL3, HDMI5.SHELL4, HDMI6.2, HDMI6.5, HDMI6.8, HDMI6.11, HDMI6.13, HDMI6.14, HDMI6.17, HDMI6.18, HDMI6.19, HDMI6.SHELL1, HDMI6.SHELL2, HDMI6.SHELL3, HDMI6.SHELL4, HDMI7.2, HDMI7.5, HDMI7.8, HDMI7.11, HDMI7.13, HDMI7.14, HDMI7.17, HDMI7.18, HDMI7.19, HDMI7.SHELL1, HDMI7.SHELL2, HDMI7.SHELL3, HDMI7.SHELL4, HDMI8.2, HDMI8.5, HDMI8.8, HDMI8.11, HDMI8.13, HDMI8.14, HDMI8.17, HDMI8.18, HDMI8.19, HDMI8.SHELL1, HDMI8.SHELL2, HDMI8.SHELL3, HDMI8.SHELL4, HDMI9.2, HDMI9.5, HDMI9.8, HDMI9.11, HDMI9.13, HDMI9.14, HDMI9.17, HDMI9.18, HDMI9.19, HDMI9.SHELL1, HDMI9.SHELL2, HDMI9.SHELL3, HDMI9.SHELL4, IC1.8 (GND), IC1.12 (~EN), IC2.2 (GND), IC3.8 (GND), IC3.12 (~EN), IC4.2 (GND), IC5.8 (GND), IC5.12 (~EN), IC6.2 (GND), IC7.8 (GND), IC7.12 (~EN), IC8.2 (GND), IC9.8 (GND), IC9.12 (~EN), IC10.2 (GND), IC11.8 (GND), IC11.12 (~EN), IC12.2 (GND), IC13.8 (GND), IC13.12 (~EN), IC14.2 (GND), IC15.8 (GND), IC15.12 (~EN), IC16.2 (GND), IC17.8 (GND), IC17.12 (~EN), IC18.2 (GND), IC19.8 (GND), IC19.12 (~EN), IC20.2 (GND), IC21.7 (VEE), IC21.8 (GND), IC22.7 (VEE), IC22.8 (GND), IC23.7 (VEE), IC23.8 (GND), IC24.7 (VEE), IC24.8 (GND), IC25.7 (VEE), IC25.8 (GND), IC26.7 (VEE), IC26.8 (GND), IC27.7 (VEE), IC27.8 (GND), IC28.7 (VEE), IC28.8 (GND), IC29.GND, IC30.3 (GND), JP1.1, JP2.1, JP3.1, JP4.1, JP5.1, JP6.1, JP7.1, JP8.1, JP9.1, JP10.1, JP11.1, JP12.1, JP13.1, MOD1.1 (GND), MOD1.10 (GND2), R2.1, R4.1, R6.1, R8.1, R10.1, R25.1, R31.1, R33.1, R35.1, R37.1, R39.1, R41.1, R43.1, R45.1, R47.1, R49.1, R51.1, R53.1, R55.1, R57.1, R59.1, R61.1, R63.1, R65.1, R67.1, R69.1, R71.1, R73.1, R75.1, R77.1, R79.1, SJ1.2, SJ2.2, SJ3.1, SJ4.1, SJ5.1, SJ6.2, SJ7.2, SJ8.2, SJ9.2, SJ10.2, SJ11.2, SJ12.2, TP2.P$1
unnamed: D1.A, R21.1
unnamed: D2.A, R22.1
unnamed: D3.A, R23.1
unnamed: D4.A, R24.1
unnamed: D9.C, SJ13.1
unnamed: D5.A, R26.1
unnamed: D6.A, R27.1
unnamed: D7.A, R28.1
unnamed: D8.A, R29.1
unnamed: R25.2, SJ13.2
unnamed: D1.C, D2.C, D3.C, D4.C, SJ11.1
unnamed: D5.C, D6.C, D7.C, D8.C, SJ12.1
unnamed: HDMI1.10, IC3.10 (DOUT3+)
unnamed: HDMI1.12, IC3.11 (DOUT3-)
unnamed: HDMI1.7, IC3.6 (DOUT2+)
unnamed: HDMI1.9, IC3.5 (DOUT2-)
unnamed: HDMI1.15, IC3.14 (DOUT4+)
unnamed: HDMI1.16, IC3.13 (DOUT4-)
unnamed: HDMI1.6, IC3.3 (DOUT1-)
unnamed: HDMI1.4, IC3.2 (DOUT1+)
unnamed: HDMI2.10, IC5.10 (DOUT3+)
unnamed: HDMI2.12, IC5.11 (DOUT3-)
unnamed: HDMI2.7, IC5.6 (DOUT2+)
unnamed: HDMI2.9, IC5.5 (DOUT2-)
unnamed: HDMI2.15, IC5.14 (DOUT4+)
unnamed: HDMI2.16, IC5.13 (DOUT4-)
unnamed: HDMI2.6, IC5.3 (DOUT1-)
unnamed: HDMI2.4, IC5.2 (DOUT1+)
unnamed: HDMI3.10, IC7.10 (DOUT3+)
unnamed: HDMI3.12, IC7.11 (DOUT3-)
unnamed: HDMI3.7, IC7.6 (DOUT2+)
unnamed: HDMI3.9, IC7.5 (DOUT2-)
unnamed: HDMI3.15, IC7.14 (DOUT4+)
unnamed: HDMI3.16, IC7.13 (DOUT4-)
unnamed: HDMI3.6, IC7.3 (DOUT1-)
unnamed: HDMI3.4, IC7.2 (DOUT1+)
unnamed: HDMI4.10, IC9.10 (DOUT3+)
unnamed: HDMI4.12, IC9.11 (DOUT3-)
unnamed: HDMI4.7, IC9.6 (DOUT2+)
unnamed: HDMI4.9, IC9.5 (DOUT2-)
unnamed: HDMI4.15, IC9.14 (DOUT4+)
unnamed: HDMI4.16, IC9.13 (DOUT4-)
unnamed: HDMI4.6, IC9.3 (DOUT1-)
unnamed: HDMI4.4, IC9.2 (DOUT1+)
unnamed: HDMI5.10, IC11.10 (DOUT3+)
unnamed: HDMI5.12, IC11.11 (DOUT3-)
unnamed: HDMI5.7, IC11.6 (DOUT2+)
unnamed: HDMI5.9, IC11.5 (DOUT2-)
unnamed: HDMI5.15, IC11.14 (DOUT4+)
unnamed: HDMI5.16, IC11.13 (DOUT4-)
unnamed: HDMI5.6, IC11.3 (DOUT1-)
unnamed: HDMI5.4, IC11.2 (DOUT1+)
unnamed: HDMI6.10, IC13.10 (DOUT3+)
unnamed: HDMI6.12, IC13.11 (DOUT3-)
unnamed: HDMI6.7, IC13.6 (DOUT2+)
unnamed: HDMI6.9, IC13.5 (DOUT2-)
unnamed: HDMI6.15, IC13.14 (DOUT4+)
unnamed: HDMI6.16, IC13.13 (DOUT4-)
unnamed: HDMI6.6, IC13.3 (DOUT1-)
unnamed: HDMI6.4, IC13.2 (DOUT1+)
unnamed: HDMI7.10, IC15.10 (DOUT3+)
unnamed: HDMI7.12, IC15.11 (DOUT3-)
unnamed: HDMI7.7, IC15.6 (DOUT2+)
unnamed: HDMI7.9, IC15.5 (DOUT2-)
unnamed: HDMI7.15, IC15.14 (DOUT4+)
unnamed: HDMI7.16, IC15.13 (DOUT4-)
unnamed: HDMI7.6, IC15.3 (DOUT1-)
unnamed: HDMI7.4, IC15.2 (DOUT1+)
unnamed: HDMI8.10, IC17.10 (DOUT3+)
unnamed: HDMI8.12, IC17.11 (DOUT3-)
unnamed: HDMI8.7, IC17.6 (DOUT2+)
unnamed: HDMI8.9, IC17.5 (DOUT2-)
unnamed: HDMI8.15, IC17.14 (DOUT4+)
unnamed: HDMI8.16, IC17.13 (DOUT4-)
unnamed: HDMI8.6, IC17.3 (DOUT1-)
unnamed: HDMI8.4, IC17.2 (DOUT1+)
unnamed: HDMI9.10, IC19.10 (DOUT3+)
unnamed: HDMI9.12, IC19.11 (DOUT3-)
unnamed: HDMI9.7, IC19.6 (DOUT2+)
unnamed: HDMI9.9, IC19.5 (DOUT2-)
unnamed: HDMI9.15, IC19.14 (DOUT4+)
unnamed: HDMI9.16, IC19.13 (DOUT4-)
unnamed: HDMI9.6, IC19.3 (DOUT1-)
unnamed: HDMI9.4, IC19.2 (DOUT1+)
PGOOD_0: IC1.15 (DIN4), JP2.6, R11.1, SJ1.1
PGOOD_0_P: HDMI0.15, IC1.14 (DOUT4+)
PGOOD_1: IC3.15 (DIN4), JP2.5, R12.1, SJ2.1
PGOOD_2: IC5.15 (DIN4), JP2.4, R13.1, SJ3.2
PGOOD_3: IC7.15 (DIN4), JP2.3, R14.1, SJ4.2
PGOOD_4: IC9.15 (DIN4), JP2.2, R15.1, SJ5.2
PGOOD_5: IC11.15 (DIN4), JP11.6, R16.1, SJ6.1
PGOOD_6: IC13.15 (DIN4), JP11.5, R17.1, SJ7.1
PGOOD_7: IC15.15 (DIN4), JP11.4, R18.1, SJ8.1
PGOOD_8: IC17.15 (DIN4), JP11.3, R19.1, SJ9.1
PGOOD_9: IC19.15 (DIN4), JP11.2, R20.1, SJ10.1
PGOOG_0_N: HDMI0.16, IC1.13 (DOUT4-)
S0: IC21.11 (S0), IC22.11 (S0), IC23.11 (S0), IC24.11 (S0), IC25.11 (S0), IC26.11 (S0), IC27.11 (S0), IC28.11 (S0), JP1.6, R21.2
S1: IC21.10 (S1), IC22.10 (S1), IC23.10 (S1), IC24.10 (S1), IC25.10 (S1), IC26.10 (S1), IC27.10 (S1), IC28.10 (S1), JP1.5, R22.2
S2: IC21.9 (S2), IC22.9 (S2), IC23.9 (S2), IC24.9 (S2), IC25.9 (S2), IC26.9 (S2), IC27.9 (S2), IC28.9 (S2), JP1.4, R23.2
S3: IC21.6 (!E), IC23.6 (!E), IC25.6 (!E), IC27.6 (!E), IC30.2 (A), JP1.3, R24.2
TCK: IC21.3 (Z), IC22.3 (Z), MOD1.2 (TCK), R26.2
TCK_0: IC1.1 (DIN1), IC21.13 (Y0), R1.1, R2.2
TCK_0_NEG: HDMI0.6, IC1.3 (DOUT1-)
TCK_0_POS: HDMI0.4, IC1.2 (DOUT1+)
TCK_1: IC3.1 (DIN1), IC21.14 (Y1), R7.1, R8.2
TCK_2: IC5.1 (DIN1), IC21.15 (Y2), R32.1, R33.2
TCK_3: IC7.1 (DIN1), IC21.12 (Y3), R38.1, R39.2
TCK_4: IC9.1 (DIN1), IC21.1 (Y4), R44.1, R45.2
TCK_5: IC21.5 (Y5), JP3.6
TCK_5_2: IC11.1 (DIN1), JP4.6, R50.1, R51.2
TCK_6: IC21.2 (Y6), JP3.5
TCK_6_2: IC13.1 (DIN1), JP4.5, R56.1, R57.2
TCK_7: IC21.4 (Y7), JP3.4
TCK_7_2: IC15.1 (DIN1), JP4.4, R62.1, R63.2
TCK_8: IC22.13 (Y0), JP3.3
TCK_8_2: IC17.1 (DIN1), JP4.3, R68.1, R69.2
TCK_9: IC22.14 (Y1), JP3.2
TCK_9_2: IC19.1 (DIN1), JP4.2, R74.1, R75.2
TDI: IC23.3 (Z), IC24.3 (Z), MOD1.3 (TDI), R27.2
TDI_0: IC1.9 (DIN3), IC23.13 (Y0), R5.1, R6.2
TDI_0_N: HDMI0.12, IC1.11 (DOUT3-)
TDI_0_P: HDMI0.10, IC1.10 (DOUT3+)
TDI_1: IC3.9 (DIN3), IC23.14 (Y1), R30.1, R31.2
TDI_2: IC5.9 (DIN3), IC23.15 (Y2), R36.1, R37.2
TDI_3: IC7.9 (DIN3), IC23.12 (Y3), R42.1, R43.2
TDI_4: IC9.9 (DIN3), IC23.1 (Y4), R48.1, R49.2
TDI_5: IC23.5 (Y5), JP5.6
TDI_5_2: IC11.9 (DIN3), JP6.6, R54.1, R55.2
TDI_6: IC23.2 (Y6), JP5.5
TDI_6_2: IC13.9 (DIN3), JP6.5, R60.1, R61.2
TDI_7: IC23.4 (Y7), JP5.4
TDI_7_2: IC15.9 (DIN3), JP6.4, R66.1, R67.2
TDI_8: IC24.13 (Y0), JP5.3
TDI_8_2: IC17.9 (DIN3), JP6.3, R72.1, R73.2
TDI_9: IC24.14 (Y1), JP5.2
TDI_9_2: IC19.9 (DIN3), JP6.2, R78.1, R79.2
TDO: IC27.3 (Z), IC28.3 (Z), MOD1.8 (TDO), R29.2
TDO_0: IC2.5 (R), IC27.13 (Y0)
TDO_0_N: HDMI0.3, IC2.4 (B)
TDO_0_P: HDMI0.1, IC2.3 (A)
TDO_1: IC4.5 (R), IC27.14 (Y1)
TDO_1_N: HDMI1.3, IC4.4 (B)
TDO_1_P: HDMI1.1, IC4.3 (A)
TDO_2: IC6.5 (R), IC27.15 (Y2)
TDO_2_N: HDMI2.3, IC6.4 (B)
TDO_2_P: HDMI2.1, IC6.3 (A)
TDO_3: IC8.5 (R), IC27.12 (Y3)
TDO_3_N: HDMI3.3, IC8.4 (B)
TDO_3_P: HDMI3.1, IC8.3 (A)
TDO_4: IC10.5 (R), IC27.1 (Y4)
TDO_4_N: HDMI4.3, IC10.4 (B)
TDO_4_P: HDMI4.1, IC10.3 (A)
TDO_5: IC27.5 (Y5), JP9.6
TDO_5_2: IC12.5 (R), JP10.6
TDO_5_N: HDMI5.3, IC12.4 (B)
TDO_5_P: HDMI5.1, IC12.3 (A)
TDO_6: IC27.2 (Y6), JP9.5
TDO_6_2: IC14.5 (R), JP10.5
TDO_6_N: HDMI6.3, IC14.4 (B)
TDO_6_P: HDMI6.1, IC14.3 (A)
TDO_7: IC27.4 (Y7), JP9.4
TDO_7_2: IC16.5 (R), JP10.4
TDO_7_N: HDMI7.3, IC16.4 (B)
TDO_7_P: HDMI7.1, IC16.3 (A)
TDO_8: IC28.13 (Y0), JP9.3
TDO_8_2: IC18.5 (R), JP10.3
TDO_8_N: HDMI8.3, IC18.4 (B)
TDO_8_P: HDMI8.1, IC18.3 (A)
TDO_9: IC28.14 (Y1), JP9.2
TDO_9_2: IC20.5 (R), JP10.2
TDO_9_N: HDMI9.3, IC20.4 (B)
TDO_9_P: HDMI9.1, IC20.3 (A)
TMS: IC25.3 (Z), IC26.3 (Z), MOD1.4 (TMS), R28.2
TMS_0: IC1.7 (DIN2), IC25.13 (Y0), R3.1, R4.2
TMS_0_N: HDMI0.9, IC1.5 (DOUT2-)
TMS_0_P: HDMI0.7, IC1.6 (DOUT2+)
TMS_1: IC3.7 (DIN2), IC25.14 (Y1), R9.1, R10.2
TMS_2: IC5.7 (DIN2), IC25.15 (Y2), R34.1, R35.2
TMS_3: IC7.7 (DIN2), IC25.12 (Y3), R40.1, R41.2
TMS_4: IC9.7 (DIN2), IC25.1 (Y4), R46.1, R47.2
TMS_5: IC25.5 (Y5), JP7.6
TMS_5_2: IC11.7 (DIN2), JP8.6, R52.1, R53.2
TMS_6: IC25.2 (Y6), JP7.5
TMS_6_2: IC13.7 (DIN2), JP8.5, R58.1, R59.2
TMS_7: IC25.4 (Y7), JP7.4
TMS_7_2: IC15.7 (DIN2), JP8.4, R64.1, R65.2
TMS_8: IC26.13 (Y0), JP7.3
TMS_8_2: IC17.7 (DIN2), JP8.3, R70.1, R71.2
TMS_9: IC26.14 (Y1), JP7.2
TMS_9_2: IC19.7 (DIN2), JP8.2, R76.1, R77.2

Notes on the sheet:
ADDRESS INPUT FROM CONTROLLER
Change Log from V1
Replaced DS90C031 (5V) with DS90LV031ATMX (3v3)
Removed redundant 100R terminators on SN65LVDT2 ICs
Added SJ 11, 12 & 13 to deactivate diagnostic LEDs
Added weak pull-downs on multiplexer outputs and positions for weak pull-ups instead.
Added 5v supply to address input to provide external power
Changed electrolytic caps to tantalum for more stable ESR with temperature to ensure 3.3v regulator stability
Removed spare mounting hole
Rerouted GND traces between pins of HDMI connectors
Change Log from V3
V3 used 'Cream' layer to generate solder mask which left NO solder jumpers covered. V4 uses 'Stop' layer instead.

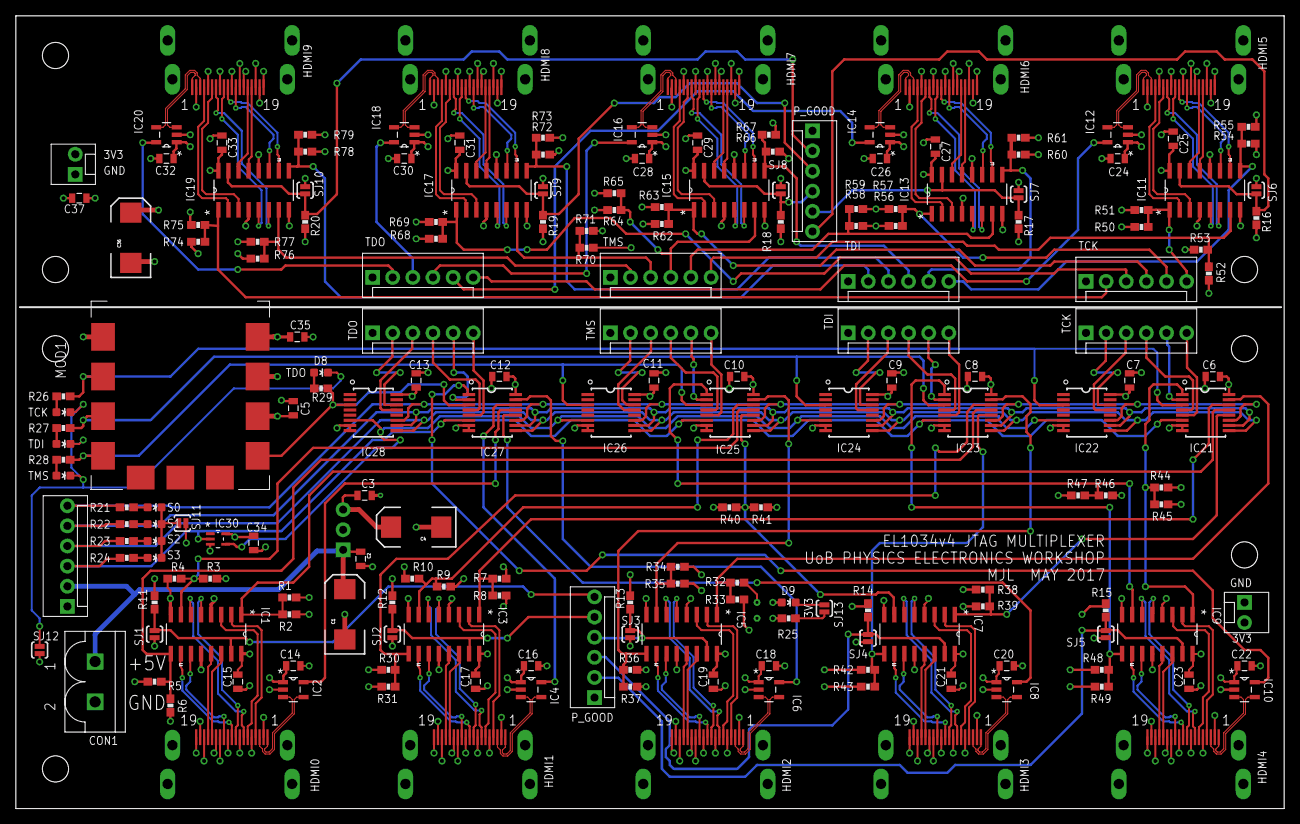
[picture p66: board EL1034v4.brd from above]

Board: 4 copper layers, 160.0 x 100.0 mm, 202 parts (1 on the bottom side), 194 nets.

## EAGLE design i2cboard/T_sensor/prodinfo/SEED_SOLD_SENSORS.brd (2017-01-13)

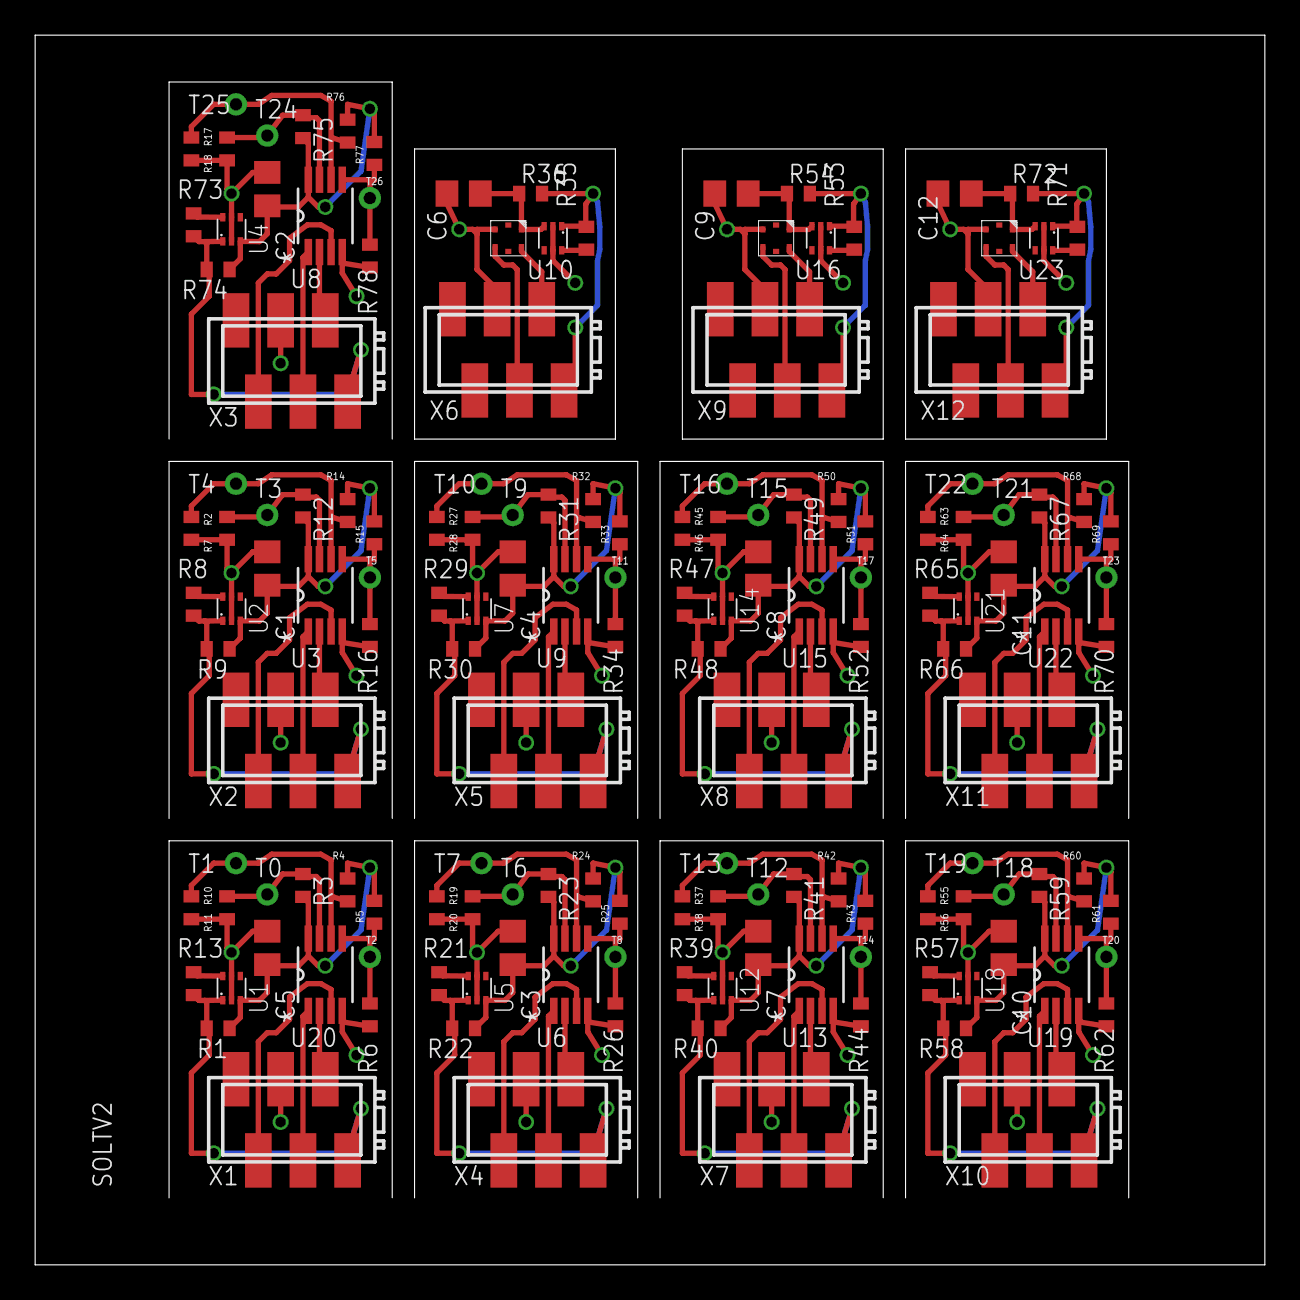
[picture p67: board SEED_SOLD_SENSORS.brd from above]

Board: 2 copper layers, 70.0 x 70.0 mm, 153 parts (0 on the bottom side), 108 nets.

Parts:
C1, C2, C3, C4, C5, C6, C7, C8, C9, C10, C11, C12: 100n; C0805
R1, R9, R22, R30, R40, R48, R58, R66, R74: 0R; R0402
R2, R6, R7, R10, R11, R16, R17, R18, R19, R20, R26, R27, R28, R34, R37, R38, R44, R45, R46, R52, R55, R56, R62, R63, R64, R70, R78: 1K; R0402
R3, R4, R5, R8, R12, R13, R14, R15, R21, R23, R24, R25, R29, R31, R32, R33, R35, R36, R39, R41, R42, R43, R47, R49, R50, R51, R53, R54, R57, R59, R60, R61, R65, R67, R68, R69, R71, R72, R73, R75, R76, R77: 10K; R0402
T0, T1, T2, T3, T4, T5, T6, T7, T8, T9, T10, T11, T12, T13, T14, T15, T16, T17, T18, T19, T20, T21, T22, T23, T24, T25, T26: UA_TPPAD1-13; UA_P1-13
U1, U2, U4, U5, U7, U10, U12, U14, U16, U18, U21, U23: NCP170_3V3; SOT563
U3, U6, U8, U9, U13, U15, U19, U20, U22: AT30TSE752-XM8-B; SOP65P490X110-8N
U11, U17, U24: HTS221; HLGA-6
X1, X2, X3, X4, X5, X6, X7, X8, X9, X10, X11, X12: MICROMATCH-6SMD; MICROMATCH_SMD-6

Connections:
GND: C5.1, R6.1, R10.1, R11.1, U1.2, U1.5, U20.4, X1.4
GND1: C1.1, R2.1, R7.1, R16.1, U2.2, U2.5, U3.4, X2.4
GND2: C2.1, R17.1, R18.1, R78.1, U4.2, U4.5, U8.4, X3.4
GND3: C3.1, R19.1, R20.1, R26.1, U5.2, U5.5, U6.4, X4.4
GND4: C4.1, R27.1, R28.1, R34.1, U7.2, U7.5, U9.4, X5.4
GND5: C6.1, U10.2, U10.5, U11.5, X6.4
GND6: C7.1, R37.1, R38.1, R44.1, U12.2, U12.5, U13.4, X7.4
GND7: C8.1, R45.1, R46.1, R52.1, U14.2, U14.5, U15.4, X8.4
GND8: C9.1, U16.2, U16.5, U17.5, X9.4
GND9: C10.1, R55.1, R56.1, R62.1, U18.2, U18.5, U19.4, X10.4
GND10: C11.1, R63.1, R64.1, R70.1, U21.2, U21.5, U22.4, X11.4
GND11: C12.1, U23.2, U23.5, U24.5, X12.4
unnamed: R5.1, R6.2, T2.TP, U20.5
unnamed: R4.1, R11.2, T1.TP, U20.6
unnamed: R3.1, R10.2, T0.TP, U20.7
unnamed: R8.1, U2.6
unnamed: R15.1, R16.2, T5.TP, U3.5
unnamed: R7.2, R14.1, T4.TP, U3.6
unnamed: R13.1, U1.6
unnamed: R2.2, R12.1, T3.TP, U3.7
unnamed: R73.1, U4.6
unnamed: R21.1, U5.6
unnamed: R25.1, R26.2, T8.TP, U6.5
unnamed: R20.2, R24.1, T7.TP, U6.6
unnamed: R19.2, R23.1, T6.TP, U6.7
unnamed: R29.1, U7.6
unnamed: R33.1, R34.2, T11.TP, U9.5
unnamed: R28.2, R32.1, T10.TP, U9.6
unnamed: R27.2, R31.1, T9.TP, U9.7
unnamed: R35.1, U10.6
unnamed: R39.1, U12.6
unnamed: R43.1, R44.2, T14.TP, U13.5
unnamed: R38.2, R42.1, T13.TP, U13.6
unnamed: R37.2, R41.1, T12.TP, U13.7
unnamed: R47.1, U14.6
unnamed: R51.1, R52.2, T17.TP, U15.5
unnamed: R46.2, R50.1, T16.TP, U15.6
unnamed: R45.2, R49.1, T15.TP, U15.7
unnamed: R53.1, U16.6
unnamed: R57.1, U18.6
unnamed: R61.1, R62.2, T20.TP, U19.5
unnamed: R56.2, R60.1, T19.TP, U19.6
unnamed: R55.2, R59.1, T18.TP, U19.7
unnamed: R65.1, U21.6
unnamed: R69.1, R70.2, T23.TP, U22.5
unnamed: R64.2, R68.1, T22.TP, U22.6
unnamed: R63.2, R67.1, T21.TP, U22.7
unnamed: R71.1, U23.6
unnamed: R77.1, R78.2, T26.TP, U8.5
unnamed: R18.2, R76.1, T25.TP, U8.6
unnamed: R17.2, R75.1, T24.TP, U8.7
SCL_L: U20.2, X1.2
SCL_L1: U3.2, X2.2
SCL_L2: U8.2, X3.2
SCL_L3: U6.2, X4.2
SCL_L4: U9.2, X5.2
SCL_L5: U11.2, X6.2
SCL_L6: U13.2, X7.2
SCL_L7: U15.2, X8.2
SCL_L8: U17.2, X9.2
SCL_L9: U19.2, X10.2
SCL_L10: U22.2, X11.2
SCL_L11: U24.2, X12.2
SDA_L: U20.1, X1.3
SDA_L1: U3.1, X2.3
SDA_L2: U8.1, X3.3
SDA_L3: U6.1, X4.3
SDA_L4: U9.1, X5.3
SDA_L5: U11.4, X6.3
SDA_L6: U13.1, X7.3
SDA_L7: U15.1, X8.3
SDA_L8: U17.4, X9.3
SDA_L9: U19.1, X10.3
SDA_L10: U22.1, X11.3
SDA_L11: U24.4, X12.3
TALERT: U20.3, X1.5
TALERT1: U3.3, X2.5
TALERT2: U8.3, X3.5
TALERT3: U6.3, X4.5
TALERT4: U9.3, X5.5
TALERT6: U13.3, X7.5
TALERT7: U15.3, X8.5
TALERT9: U19.3, X10.5
TALERT10: U22.3, X11.5
V3_3L: C5.2, R1.1, R3.2, R4.2, R5.2, U1.3, U20.8
V3_3L1: C1.2, R9.1, R12.2, R14.2, R15.2, U2.3, U3.8
V3_3L2: C2.2, R74.1, R75.2, R76.2, R77.2, U4.3, U8.8
V3_3L3: C3.2, R22.1, R23.2, R24.2, R25.2, U5.3, U6.8
V3_3L4: C4.2, R30.1, R31.2, R32.2, R33.2, U7.3, U9.8
V3_3L5: C6.2, R36.1, U10.3, U11.1
V3_3L6: C7.2, R40.1, R41.2, R42.2, R43.2, U12.3, U13.8
V3_3L7: C8.2, R48.1, R49.2, R50.2, R51.2, U14.3, U15.8
V3_3L8: C9.2, R54.1, U16.3, U17.1
V3_3L9: C10.2, R58.1, R59.2, R60.2, R61.2, U18.3, U19.8
V3_3L10: C11.2, R66.1, R67.2, R68.2, R69.2, U21.3, U22.8
V3_3L11: C12.2, R72.1, U23.3, U24.1
V5F: R1.2, R13.2, U1.1, X1.1
V5F1: R8.2, R9.2, U2.1, X2.1
V5F2: R73.2, R74.2, U4.1, X3.1
V5F3: R21.2, R22.2, U5.1, X4.1
V5F4: R29.2, R30.2, U7.1, X5.1
V5F5: R35.2, R36.2, U10.1, X6.1
V5F6: R39.2, R40.2, U12.1, X7.1
V5F7: R47.2, R48.2, U14.1, X8.1
V5F8: R53.2, R54.2, U16.1, X9.1
V5F9: R57.2, R58.2, U18.1, X10.1
V5F10: R65.2, R66.2, U21.1, X11.1
V5F11: R71.2, R72.2, U23.1, X12.1

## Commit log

2015-07-08 Made directory for analog board simulations.
2015-09-15 beta version of the schematic 8 channels , board : analogue part execept the bias is done.
2015-09-16 schematic with output connector connected
2015-09-18 pre production PCB version
    [components.ods]
2015-09-18 PCB ready for production
    [SOL_AMPV2.brd, SOL_AMPV2.sch, components.ods]
2015-09-22 files sent for production
    [SOL_AMPV2.brd, SOL_AMPV2.sch]
2015-11-20 Comitting artwork and PCB database files
    [pc051a_toplevel_22-1-6.drl, pc051b_toplevel_42-1-6.drl, pc051b_toplevel_42.brd]
2016-01-05 added MPPC PCB proposal
2016-01-27 added dark count study
    [concidencecounts_1.ods]
2016-01-28 added mathlab script for the peak findig
    [concidencecounts_1.ods]
2016-02-02 Some photos of digital boards.
2016-02-08 Diagram of mechanics mounting idea.
2016-02-09 added more details for the electronics mounting
2016-02-09 added ground spring for analogue compartment
2016-02-10 added power supply considerations
2016-02-15 Write both boards
2016-02-16 added the operation instructions for the analogue board
2016-02-18 Made area for power supply documents.
2016-02-19 Added simple library to control bias via uC board.
2016-02-19 Starting to take SiPM calibration data.
2016-02-22 moved cabling/power supply related info to power supply dir
2016-02-22 Added David C's code for environmental chamber.
2016-02-23 Remove top two bits of samples when storing data.
2016-02-23 Allow sipmcalibrationrun.py to use trim voltages, use timestamp in filename.
2016-02-23 Read current temp before waiting.
2016-02-23 Store trim voltage in output when taking data.
2016-02-24 Working on calibration for SiPM and waveform parameters, issue #21
2016-02-26 Easy script to run multiple SiPM calibration runs at a single temperature.
2016-03-03 ADC1832 simulation with +5 , -3.3 V power supply
2016-03-10 Hopefully decent measurement of rates with estimated over voltage.
2016-03-15 Simple program to set bias DAC voltages for testing.
2016-03-18 Initial draft of electronics board specs.
2016-04-01 Added David's pin connection suggestions to spec.
2016-04-20 temp 32 a board sch
2016-04-21 analogue board design status 21 April
2016-04-26 dc patch docs
    [dccouplinginfo.ods]
2016-04-27 higher V5 and doc / production correctiions
    [dccouplinginfo.ods]
2016-05-03 updated instructions for vout+ vout - change
    [dccouplinginfo.ods]
2016-05-16 13 by 13 SiPM sensor PCB panel.
    [panel13_13-B.Cu.gbl, panel13_13-B.Mask.gbs, panel13_13-B.Paste.gbp, panel13_13-B.SilkS.gbo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]
2016-05-19 added MPPC board connection verificatoin doc
2016-05-20 new dir for original prototype design files
2016-05-30 add sub dirs for differnt versions of the analogue brd's
    [SOL_AMPV2.brd, SOL_AMPV2.sch, dccouplinginfo.ods]
2016-05-30 added datasheets serial devices, description serial devices
2016-06-09 added power supply candidates and I2C interface card info
2016-06-13 Modify I2C address of MCP4725 for Wim's test board.
2016-06-13 Allow bias = 0 V
2016-06-13 New 7 x 13 double sided SiPM PCB panel.
    [panel13x7_doublesided-B.Cu.gbl, panel13x7_doublesided-B.Mask.gbs, panel13x7_doublesided-B.SilkS.gbo, panel13x7_doublesided-Edge.Cuts.gm1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]
2016-06-14 added design doc's calcs
    [SOL_AMP3_calculations.ods, cablediameter.ods]
2016-06-14 DACs provided with 4.6 V, not 5.0.
2016-06-15 Cleaning up repo for old 13x7 panel.
    [panel13_13-B.Cu.gbl, panel13_13-B.Mask.gbs, panel13_13-B.Paste.gbp, panel13_13-B.SilkS.gbo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]
2016-06-15 Updated 13x7 panel for review.
    [panel13x7_doublesided-B.Cu.gbl, panel13x7_doublesided-B.Mask.gbs, panel13x7_doublesided-B.SilkS.gbo, panel13x7_doublesided-Edge.Cuts.gm1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]
2016-06-17 updated schematics I2c interface other info added
    [cablediameter.ods, calculations.ods, dccouplinginfo.ods]
2016-06-22 Left a space between rows, bigger fiducials, larger tabs.
    [panel13x7_doublesided.kicad_pcb]
2016-06-24 some extra info added
    [cablediameter.ods]
2016-06-24 MPPC first batch data Hamamatsu
    [160613_S12572-050P_inspection data( TrayNo1-No12).xlsx]
2016-06-27 added per tray serial nr sheet and pictures
    [160613_S12572-050P_inspection data( TrayNo1-No12).xlsx]
2016-06-28 Allow voltage scans and setting voltage with trims.
2016-06-29 added test sheet
    [testsheet.ods]
2016-06-30 Tidying up SiPM PCB area.
2016-07-04 review analogue board schematics
    [SOL_AMP3_calculations.ods, dccouplinginfo.ods, testsheet.ods]
2016-07-14 SiPm cable info, test results brd 3
    [SOL_AMP3_calculations.ods, dccouplinginfo.ods, testsheet.ods]
2016-07-22 added data sheets and change info , calculations
    [SOL_AMP3_calculations.ods]
2016-07-25 clean up , additional test info 8 ch brd
    [SOL_AMPV2.brd, SOL_AMPV2.sch, dccouplinginfo.ods, testsheet.ods]
2016-07-27 cmm test repeated
    [testsheet.ods]
2016-07-27 Added a -u / --notemp option to allow use of script without environmental chamber
2016-07-27 updated analogue board schematics and calcs
    [SOL_AMP3_calculations.ods]
2016-07-28 Script to check the accuracy of the high voltage setting
2016-07-28 Option to only read current DAC voltages.
2016-07-28 Voltage scans requested by Simon. See issue #55.
2016-08-04 Picture showing MPPC numbering for PCB panel.
2016-08-09 Pin mapping for inside the enclosure.
2016-08-23 just some extra sim circuit
2016-08-26 check dimensions amplifier board
    [SOL_AMP3_calculations.ods]
2016-08-30 correction in dimension board
    [SOL_AMP3_calculations.ods]
2016-09-01 Initial support for Gent boards.
    Frontend takes board name parameter to pick from connection list.
    Currently supported by setvoltages.py
2016-09-02 Minimial analog board temperature reading.
    Don't currently use all of temp chip registers, just read
    from the ambient temperature.
2016-09-02 Correct IP addresses for Gent boards.
2016-09-05 Untested programme to monitor temperature of test plane.
2016-09-05 Get test frame temperature sensor class.
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2016-10-17 amplifier board almost final version info
    [cablediameter.ods]
2016-10-28 Working on MPPC PCB cut outs.
    [panel13x7_doublesided.kicad_pcb]
2016-10-30 Hopefully easier to cut out.
    [panel13x7_doublesided.kicad_pcb]
2016-10-30 Updated date on silk screen.
    [panel13x7_doublesided.kicad_pcb]
2016-10-30 Removed unwated labels on SiPM PCB.
    [panel13x7_doublesided.kicad_pcb]
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2016-11-17 review cable directory and changed structure, added more info about the temperature and humidity sensor
    [SOLID_HSENSOR_bom.csv, SOLID_HSENSOR_bom.ods, SOLID_TSENSOR_BOM.csv, SOLID_TSENSOR_BOM.ods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]
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2016-12-12 small changes
    [testsheet.ods]
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2017-01-13 updated documentation after testing the PCB's for T and H sensor
    [SEED_SOLD_SENSORS.brd]
2017-01-18 added info for the TSENSOR boards
    [boardinfo.ods, testsheet.ods]
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2017-02-07 Hamamatsu sensor information.
    [160613_S12572-050P_inspectiondata_TrayNo1-No12.csv, 161114_S12572-050P_inspection data( TrayNo1-No3).xlsx, 161205_S12572-050P_inspection data( TrayNo.1-No.3).x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]
2017-02-22 added info for version 1.3 of the amplifier board
    [SOL_AMP3_calculations.ods, S_AmpTstBrd.ods, boardinfo.ods, dccouplinginfo.ods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]
2017-02-22 new SiPm cabling
    [dccouplinginfo.ods]
2017-04-07 Documentation update for the 32ch amplifier board (quotation version)
    [boardinfo.ods]
2017-04-10 Adding noise simulation for AD8132 based circuit
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2017-04-25 added modification info, added data sheets for the amplifier board
    [boardinfo.ods]
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2017-05-09 added version 2.0 production info amplifier board
    [SOL_AMP3_calculations.ods, boardinfo.ods]
2017-05-25 Adding Readme file , PCB database files ( Cadence Allegro format ) and assembly drawings for SoLiD clock board and interface FMC
    [pc054a_fmc_08.brd, pc054a_toplevel_27.brd]
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2017-06-07 Adding manufacturing files for JTAG fanout
    [EL1034v3_BoM.xls]
2017-06-20 Named batches on Hamamatsu data.
    [161114_S12572-050P_inspection_data_TrayNo1-No3_BATCH3.xlsx, 161205_S12572-050P_inspection_data_TrayNo.1-No.3_BATCH4.xlsx, 161226_S12572-050P_inspection_data_Tr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]
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2017-08-28 added data sheets for analogue board after disk change
    [SOL_AMP3_calculations.ods, boardinfo.ods, boards.ods]
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2017-10-16 Adding CAD files for JTAG board in Eagle format.
    [EL1034v4 BoM.xls, EL1034v4.brd, EL1034v4.sch]
2017-10-18 added / change info
    [boardinfo.ods]
2017-10-18 added JTAG info
    [EL1034v4 BoM.xls]
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2017-10-30 Adding CAD files and parts list for service boxes.
    [Parts lists.xlsx]
2017-11-03 * Adding Mechanical CAD files for services box. * Adding PCB design CAD files for main power PCB ( Design Spark format )
    [Solid power fan-out - Bottom Copper (Paste).gbr, Solid power fan-out - Bottom Copper (Resist).gbr, Solid power fan-out - Bottom Copper.gbr, Solid power fan-out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]
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2019-02-26 added utility box info , more data sheets and removed empty .ignore files
    [components.ods, testsheet_SOL_AMPV3.ods]
2019-06-07 updates , added 12 DC DC converter
    [components.ods]

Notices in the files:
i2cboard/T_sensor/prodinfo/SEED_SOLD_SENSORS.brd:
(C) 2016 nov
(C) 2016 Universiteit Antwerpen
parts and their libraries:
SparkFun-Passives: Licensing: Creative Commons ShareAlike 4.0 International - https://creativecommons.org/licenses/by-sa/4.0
